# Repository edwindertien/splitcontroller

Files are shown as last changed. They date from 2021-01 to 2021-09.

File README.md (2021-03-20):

# splitcontroller
code and hardware files for a split level game controller

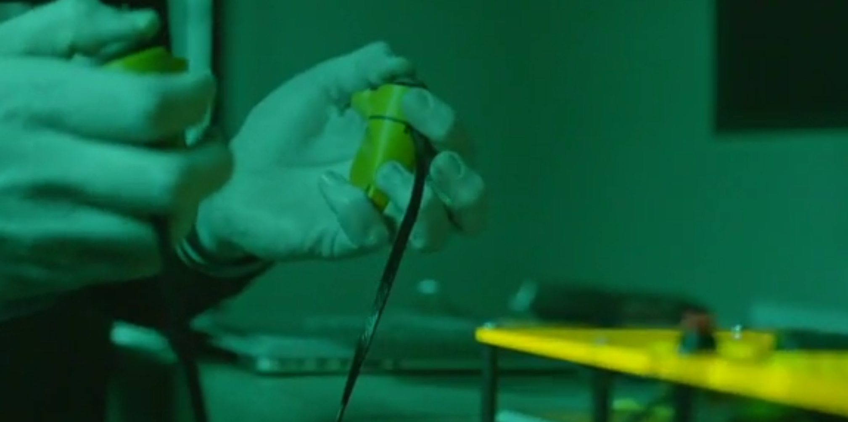
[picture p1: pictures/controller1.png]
dual hand-held controller with bridge box picture(c)IDTV(2021)
 

This project has been designed for a Duchenne patient who had progressive trouble operating his beloved regular PS4 controller. The original controller has been 'bridged' or patched by an Arduino Due (the PS4 controller works on 3.3V, so an Arduino with many inputs and outputs running at 3.3V is convenient). As new controller a split handheld system is used. This can be consisting of two Wii-nunchuck controllers or two custom 3D printed handheld controllers using (in this case) original PS4 joysticks. Currently this repository contains the following directories: 
  * bridge firmware: the firmware for the Arduino Due. Pinout is given in the header part of the code. The Wii-nunchuck functions are included in the code by Tod E. Kurt (2017) and modified for use on the DUE
  * remote arduino box: a simple laser cut 'sandwich' plate box containing a severely stripped-down ps4 controller, the arduino due and a 8000mAh powerbank. Included are some pictures and an svg file for cutting. Schematic drawing will follow. 
  * remote-modular ps4: an openSCAD script and printable STL files for a customisable hand-held design
  * remote-modular-switch: an openSCAD script and printable STL files for a customisable hand-held using the miniature nintendo-switch joystick

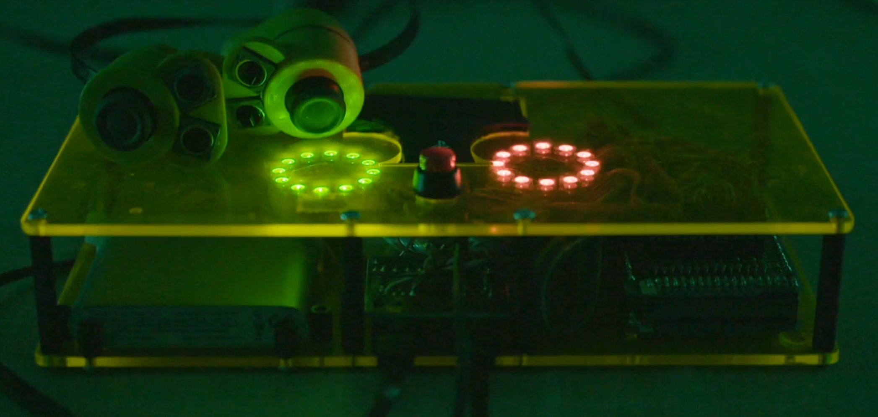
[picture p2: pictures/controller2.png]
bridge box, picture(c)IDTV(2021)
 

# bridge firmware
This code is meant for an Arduino Due which is used to take input signals from two handheld controllers, such as Wii-nunchucks or custom build controllers wired to A0--A7, and parse these signals to a modified PS4 controller. 

# remote arduino box
Simple laser cut 'sandwich' plate box containing a severely stripped-down ps4 controller, the arduino due and a 8000mAh powerbank. Further electonics consist of two 12-LED neopixel style ring-lights for feedback, a protoshield containing series resistors and RC filters for generating output signals to the PS4 controller. A small thin patching pcb for PS4 has been added to connect the Arduino due to the remnants of the PS4 controller. In order to connect two nunchucks to one I2C port, a PCA9540B I2C multiplexer has been added to the nice SMD proto-area of the used Adafruit Arduino MEGA protoshield. 

The parts used in the current version (as televised in 'We Gaan Het Maken')
  * Arduino Due
  * mega proto shield
  * 17 x resistor 1k (series resistor between outputs arduino to button inputs ps4)
  * 4 x resistor 100k (RC filter between analog outputs arduino to joystick inputs ps4)
  * 4 x capacitor 10uF (RC filter between analog outputs arduino to joystick inputs ps4)
  * PS4 remapper pcb (wired connection between arduino (shield) and ps4)
  * powerbank (8000mAh)
  * pushbutton (1 extra pushbutton to act as the PS4 button) on the box
  * 2 x RJ45 socket (to connect the custom handhelds) 

and for the handhelds:
  * 2 x flat UTP cable, 1 meter, black. 1 side has the plug, the other needs to be stripped into separate strands)
  * 3d printed parts: a handle, holder and top bit (and optional wedge)
  * a joystick. 1 option is a standard PS4 joystick (currently used) or a nintendo switch joystick (which needs a separate foil cable socket and adapter pcb to make connection) 
  * 2 x 12x14 mm pusbutton (large buttons have the easiest 'click')
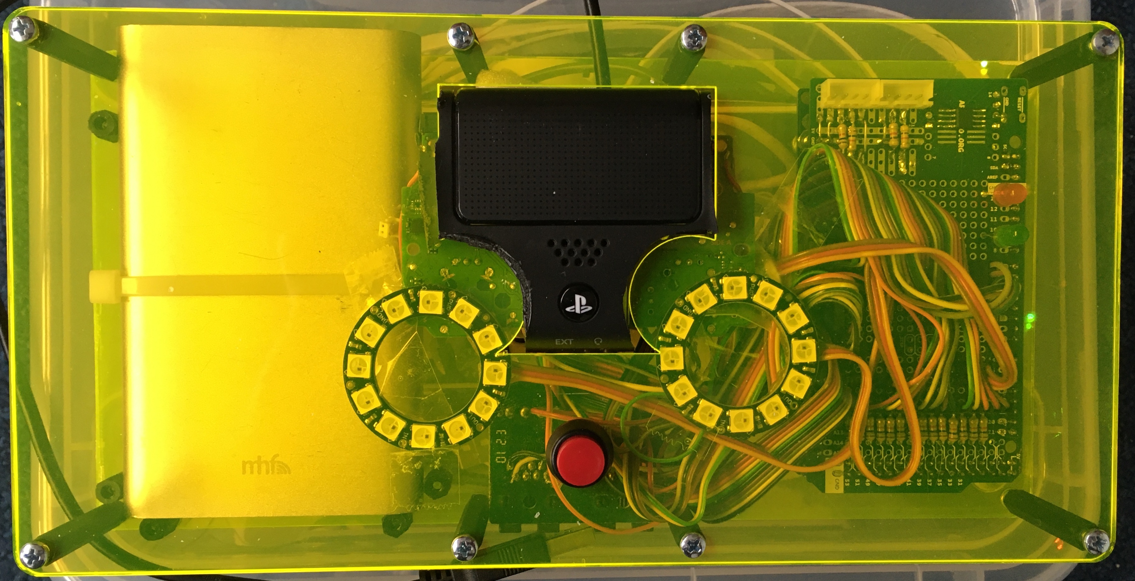
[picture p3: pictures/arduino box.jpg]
sandwich plate box with arduino, ps4 controller and powerbank
 

# remote-modular ps4
This directory contains an openSCAD script to generate a modular parametric hand-held controller using a standard PS4 joystick (replacement part) and two pushbuttons. For connectivity a flat (flexible) 6mm wide UTP cable has been used. Standard RJ45 plugs are used to connect these hand-helds to the arduino box. 

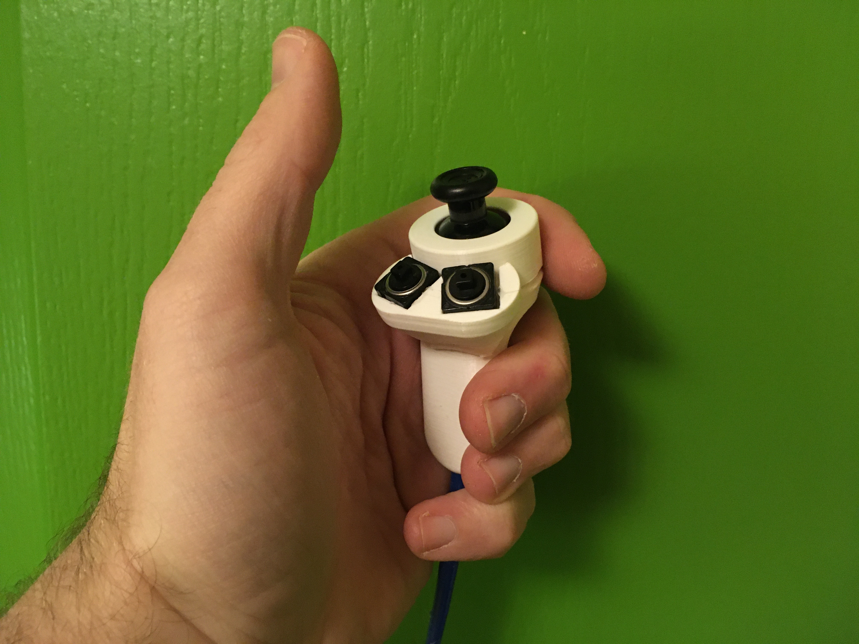
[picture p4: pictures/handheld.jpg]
3D printed handheld
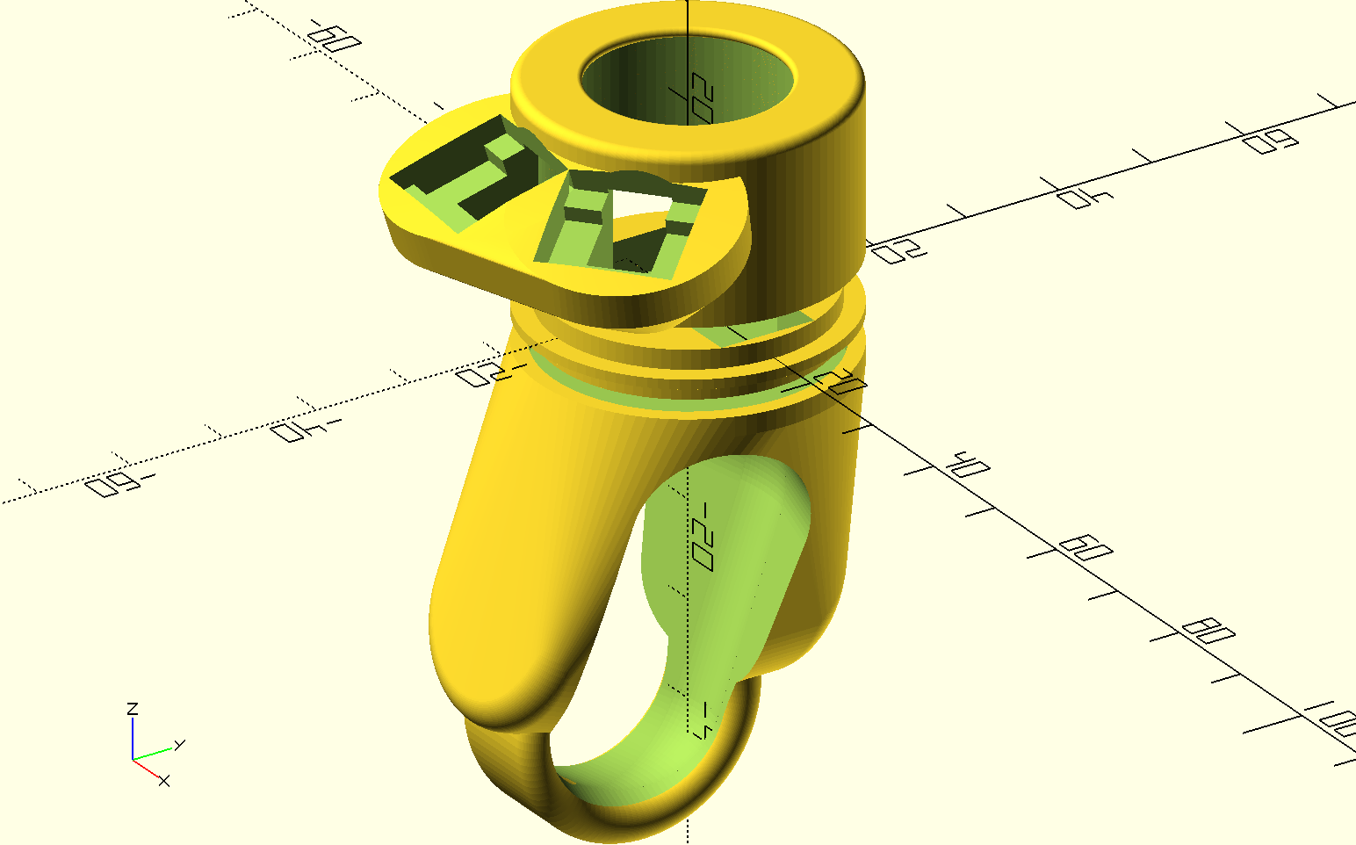
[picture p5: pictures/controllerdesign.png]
OpenSCAD design
 

# disclaimer
Hopefully stating the obvious: no guarantees can be given that these plans are correct or will work in your case or are safe. You will undoubtedly void the waranty on any PS4 controller you bought when you cut it down into functional bits and start adding wires and other functions. Re-selling any of this is probably actively prohibited by the Sony coorperation, so don't. Powering the device from a portable source such as a 5V power bank makes sense: Don't power wired handhelds with a supply directly connected to the mains. Maintain galvanic separation at all times (and if you don't know what that means, you should not be building this stuff).

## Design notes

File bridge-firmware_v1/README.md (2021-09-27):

The SD/LCD module code is used for an Arduino Due connected to a ReprapDiscount Smart Controller
This is a standard control panel for use on (for example) a Prusa MK3 printer
and contains a 4x20 character LCD display, rotary encoder, button, buzzer and SD card
slot.

The code assumes a pin-out as used on the RAMPS 1.4 arduino shield (normally for
Arduino MEGA). The only change is that on the DUE the SPI port is not mapped to pins
50, 51 and 52, but the ISP header at the center of the board has to be used

This code uses the standard built-in examples for Arduino, both for the LCD from
http://www.arduino.cc/en/Tutorial/LiquidCrystalHelloWorld
and the SD library 'file list' example.

Note that the DUE works on 3.3V but the display controller assumes 5V. It has a level
shifter (again) to operate the SD card on 3.3V. (I tried to make it work powered by 3.3V
although the display works, the SD card does not. The control board is hence powered by 5.0 V)

The following pin-out for the two 10-way EXP connectors on the display board are used:

```______________________________________
| EXP1 connector pin | Arduino DUE pin |
| 1 buzzer           | 37              |
| 2 ENCODER-button   | 35              |
| 3 LCD enable       | 17              |
| 4 LCD RS           | 16              |
| 5 LCD D4           | 23              |
| 6 LCD D5           | 25              |
| 7 LCD D6           | 27              |
| 8 LCD D7           | 29              |
| 9 GND              | GND             |
| 10 VCC             | +5V (not 3.3V!) |
|____________________|_________________|
______________________________________
| EXP2 connector pin | Arduino DUE pin |
| 1 MISO             | ISP pin 1 MISO  |
| 2 SCK              | ISP pin 3 SCK   |
| 3 ENCODER-1        | 31              |
| 4 ISP slave sel    | 53              |
| 5 ENCODER-2        | 33              |
| 6 MOSI             | ISP pin 4 MOSI  |
| 7 SD card detect   | 49              |
| 8 button           | 41              |
| 9 GND              | GND             |
| 10 NC              |                 |
|____________________|_________________|
```

(cc) e13, May 2021

************************************************************
SPLITCONTROLLER
************************************************************
Sketch for controlling a modified PS4 controller
using two nunchucks or analog nunchuck equivalent
(two hand-held controllers with two axis and two buttons)

2 nunChucks (multiplexed) using code from WiiChuckDemo by
2008 Tod E. Kurt, http://thingm.com/

Controller is Arduino Due, 1k series resistors are used
between PS4 buttons and Due outputs. All inputs are active-low
except R1, L1 and the Z-axes.

AnalogWrite is used to mimick joystick signals, RC low-pass
filters (10uF, 1k) have been used to make the analog signals

E13 - November 2020
--
```
Original nunchuck:  signal:    ext. cable    black nunchuck:
white -             ground     orange        white
red -               3.3+v      black         red
green -             data  A4   blue          blue
yellow -            clock A5   red           green

PCA 9540 pinout
      _____
SCL -|     |- SC1
SDA -|     |- SD1
VCC -|     |- GND
SD0 -|_____|- SC0
```

both the nunchucks and the PCA95040 can be powered from pins, 5V
For I2C using internal pull-up is sufficient

for the wired handheld controllers the following pinout
has been used: on RJ45 connectors:
```

1 analog_X
2 analog_Y
3 VCC
4 GND (switch)
5 GND (switch)
6 GND (potentiometer)
7 switch_1
8 switch_2
```

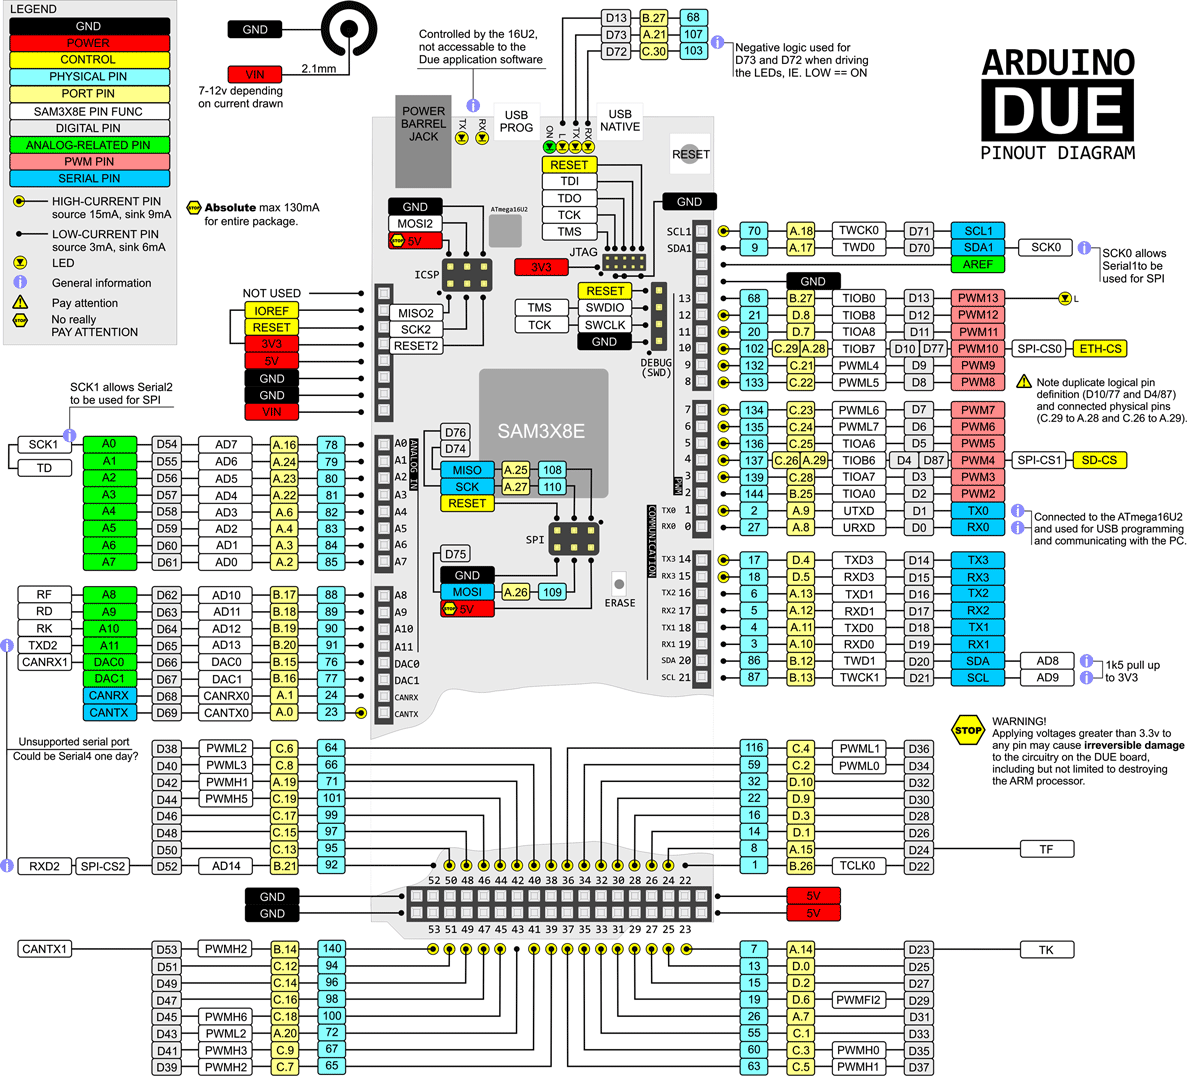
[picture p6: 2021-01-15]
remote-arduino box/documentation/Arduino-Due-Pinout.png

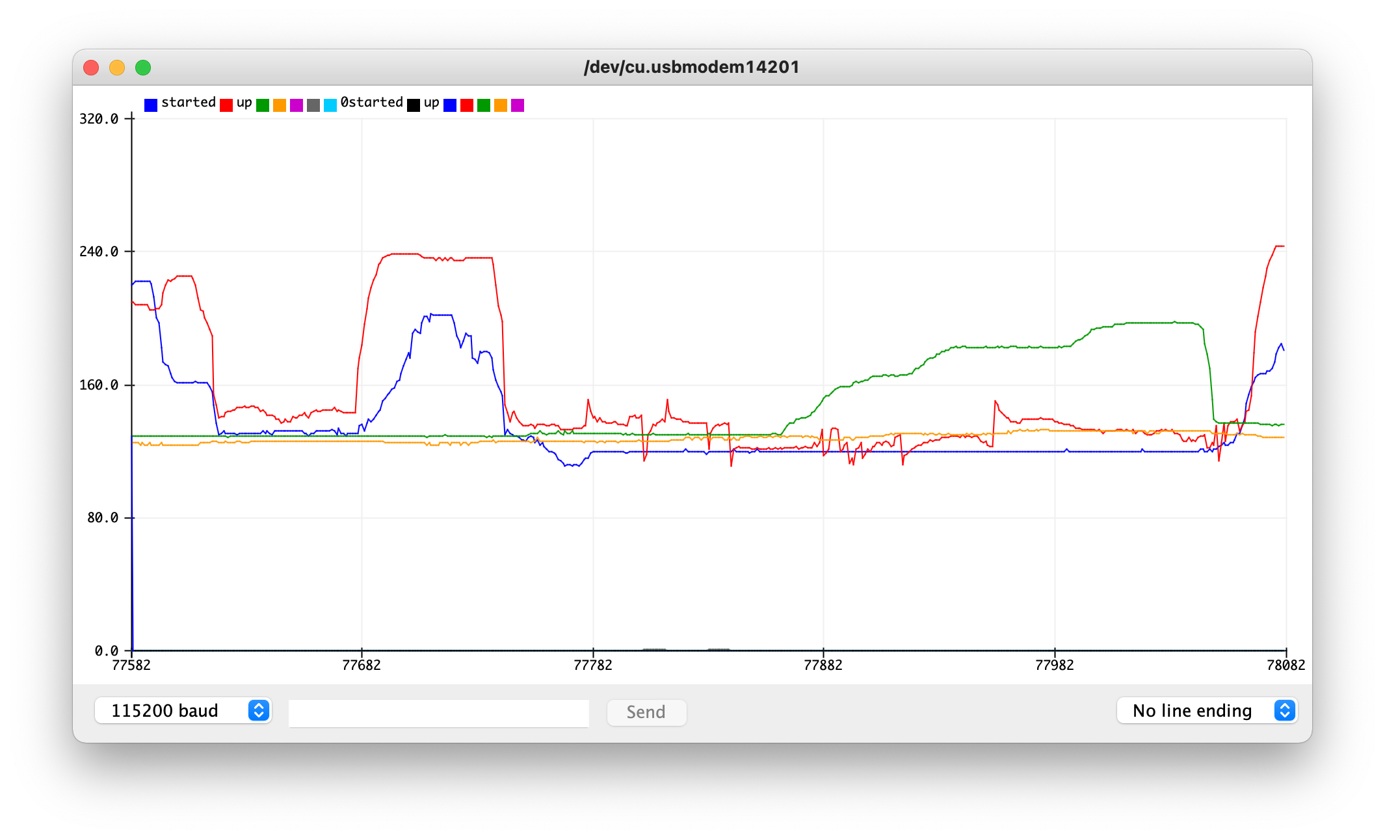
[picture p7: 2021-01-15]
pictures/analogjoystickdata.png

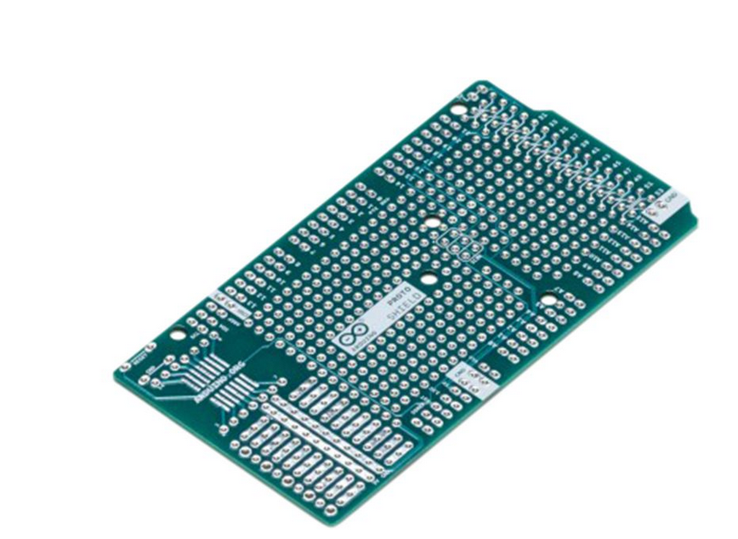
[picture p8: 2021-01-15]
pictures/protoshield.png

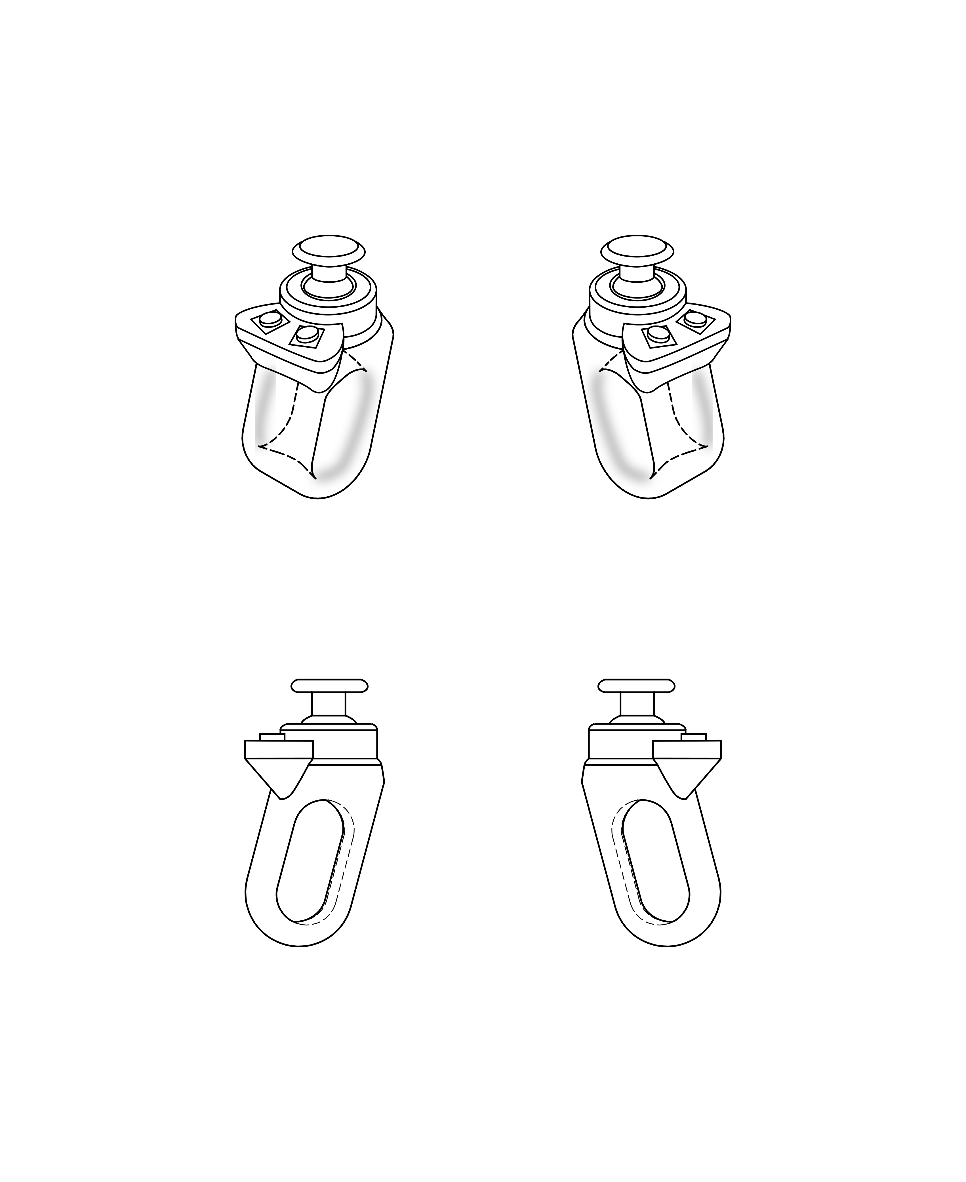
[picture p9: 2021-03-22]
pictures/new_controller_layout.png

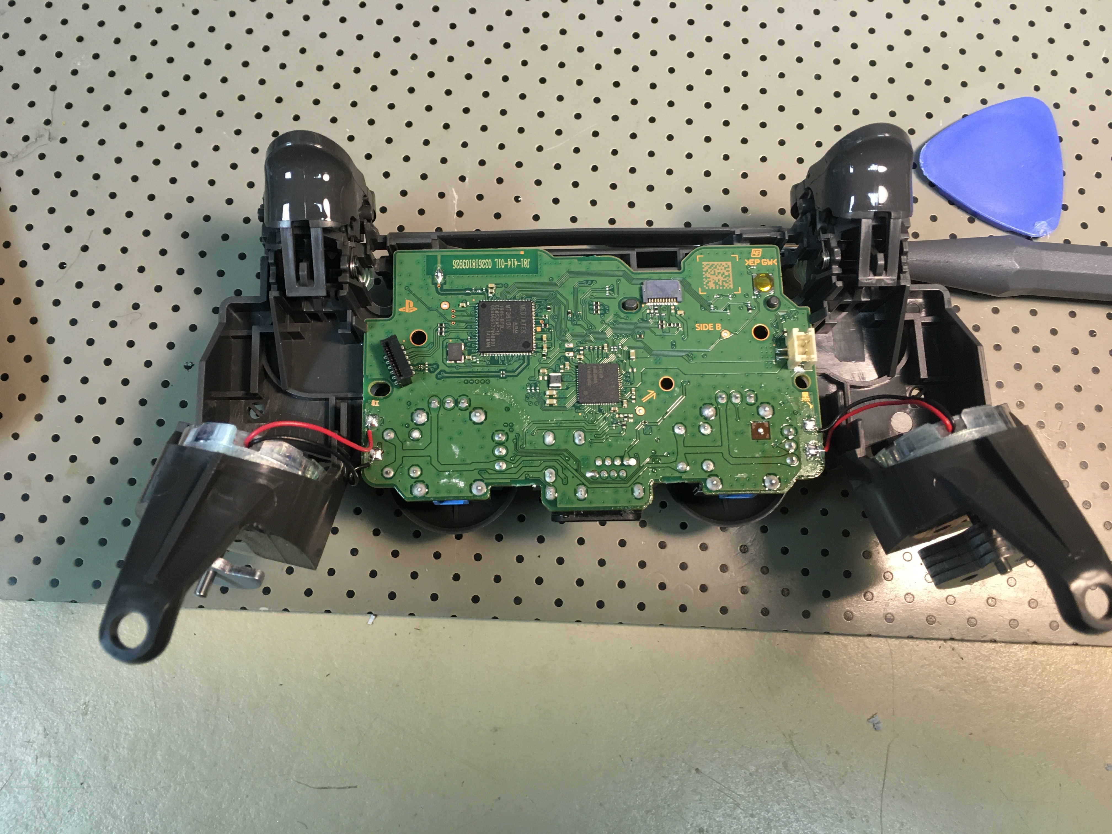
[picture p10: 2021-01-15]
pictures/strippedcontroller.jpg

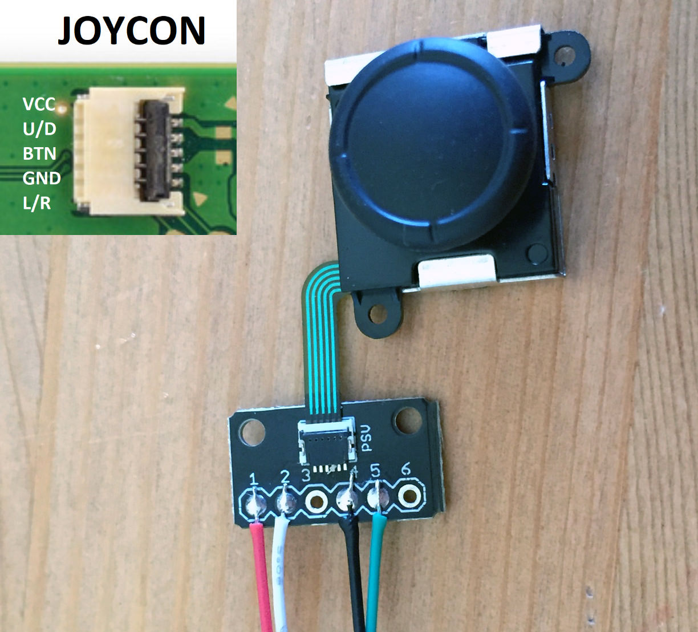
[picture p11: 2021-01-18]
remote-modular-switch/images/NAisoG4.jpg

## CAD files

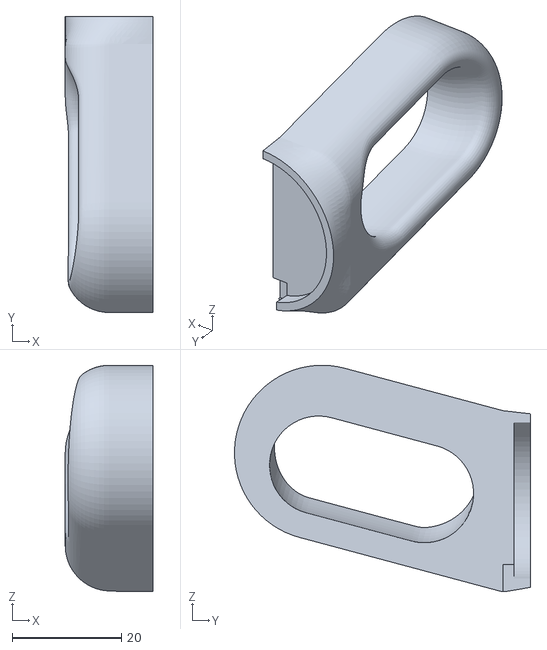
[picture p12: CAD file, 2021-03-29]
remote-modular-ps4/export/rounded_version_half_mesh1.stl
16.0 x 54.1 x 41.4

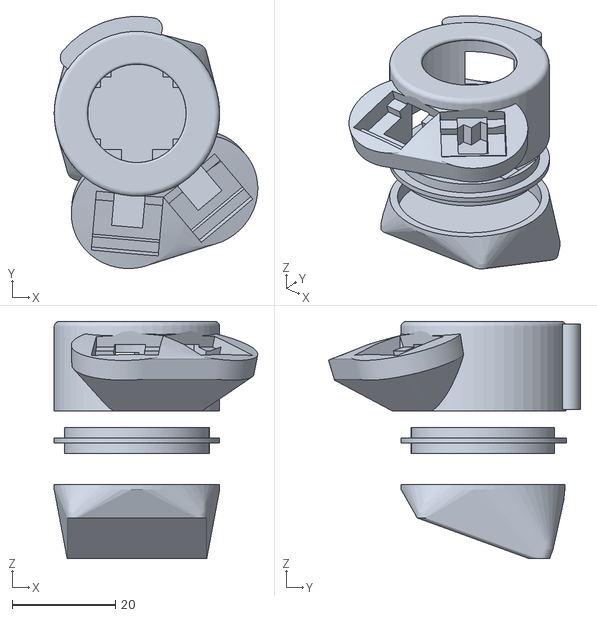
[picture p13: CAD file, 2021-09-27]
remote-modular-ps4/modularremote_adjusted_piece.stl
39.4 x 48.7 x 45.9

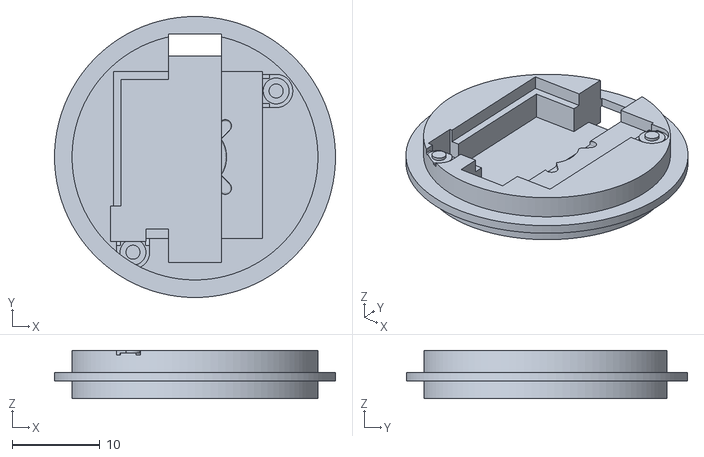
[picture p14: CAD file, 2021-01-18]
remote-modular-switch/export/switch-holder.stl
32.0 x 32.0 x 5.50

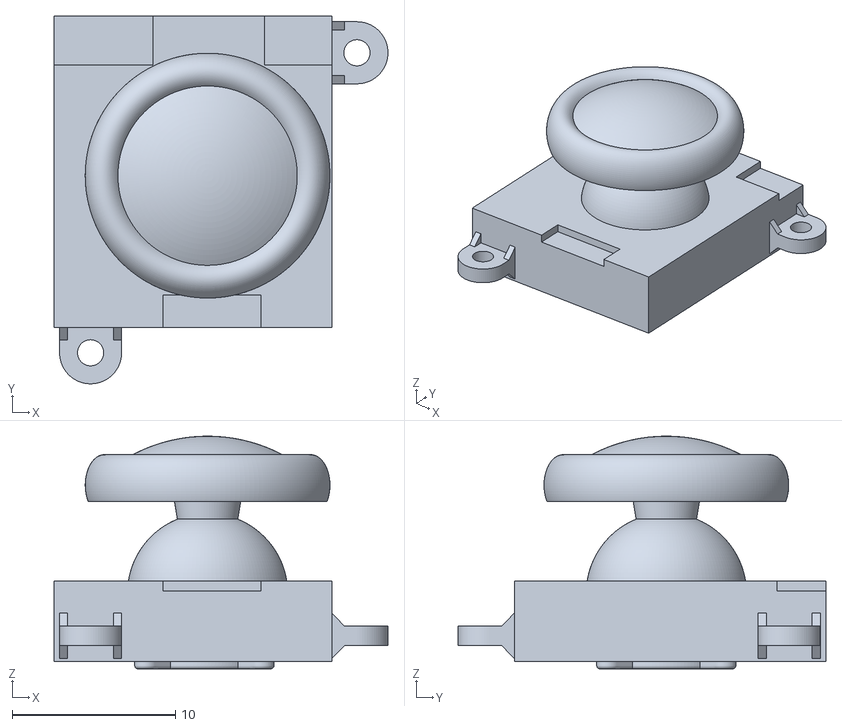
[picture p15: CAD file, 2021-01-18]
remote-modular-switch/export/joycon.stl
20.4 x 22.5 x 14.2

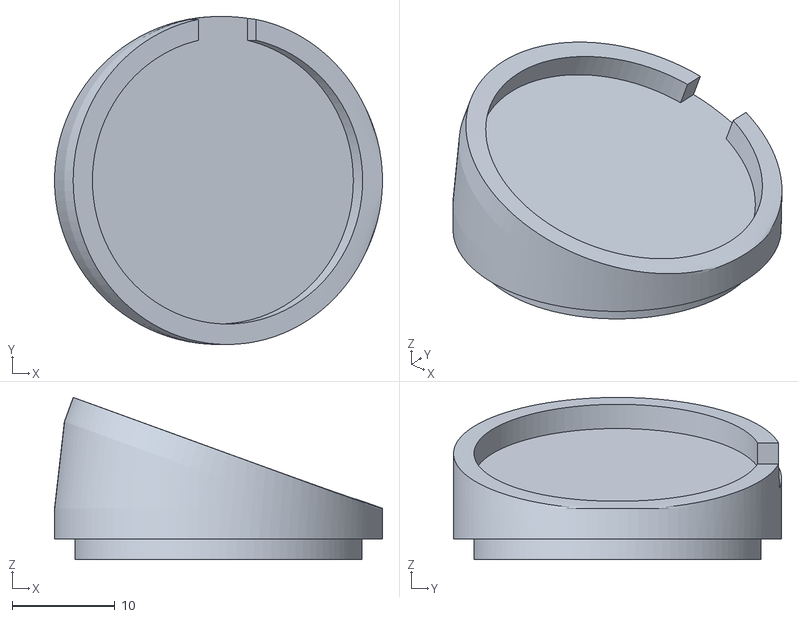
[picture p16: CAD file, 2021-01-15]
remote-modular-ps4/export/wedge20.stl
32.0 x 32.0 x 15.8

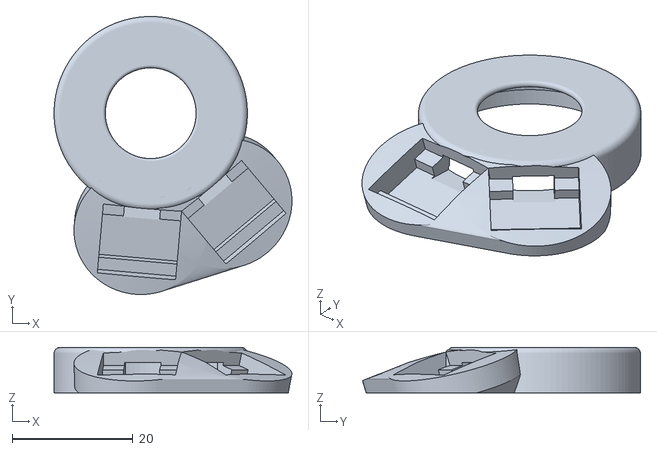
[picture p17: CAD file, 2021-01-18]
remote-modular-switch/export/switch-top.stl
39.4 x 46.0 x 7.53

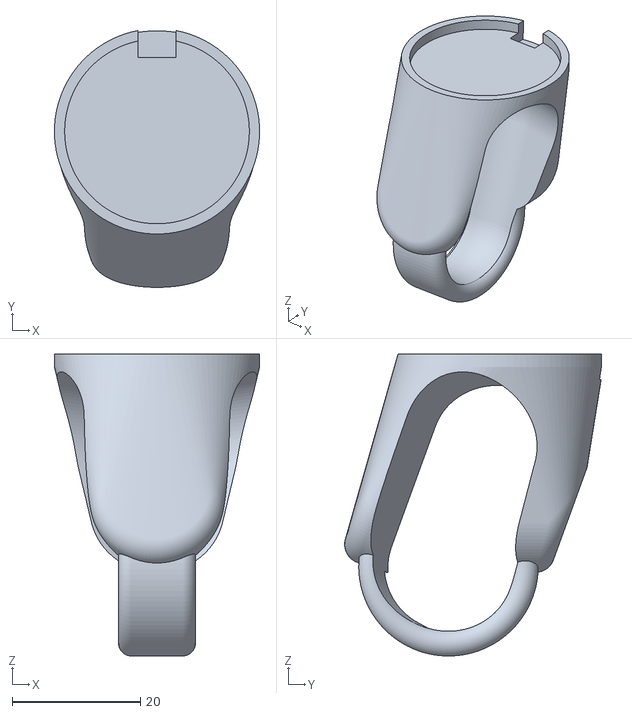
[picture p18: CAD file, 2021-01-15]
remote-modular-ps4/export/modularremote-beugelring.stl
32.0 x 40.0 x 47.1

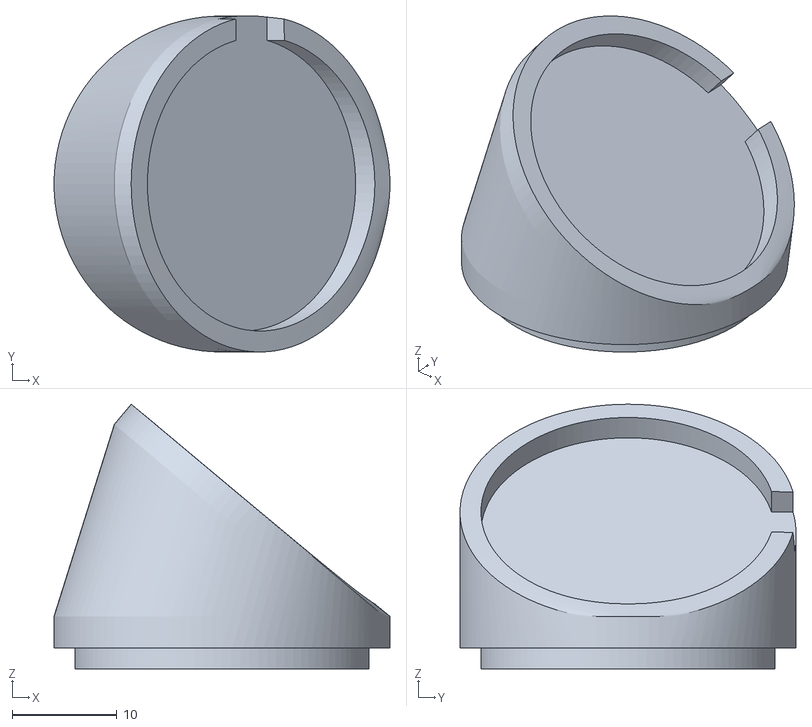
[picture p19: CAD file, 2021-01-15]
remote-modular-ps4/export/wedge40.stl
32.0 x 32.0 x 25.2

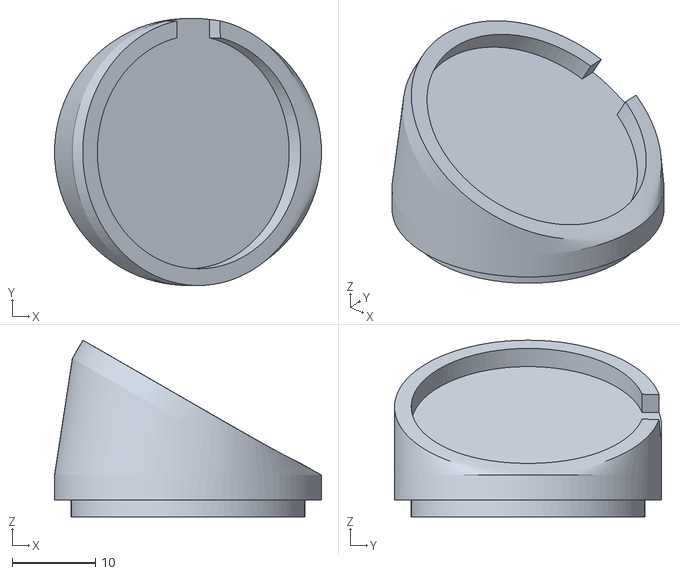
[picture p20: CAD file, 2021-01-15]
remote-modular-ps4/export/wedge30.stl
32.0 x 32.0 x 21.2

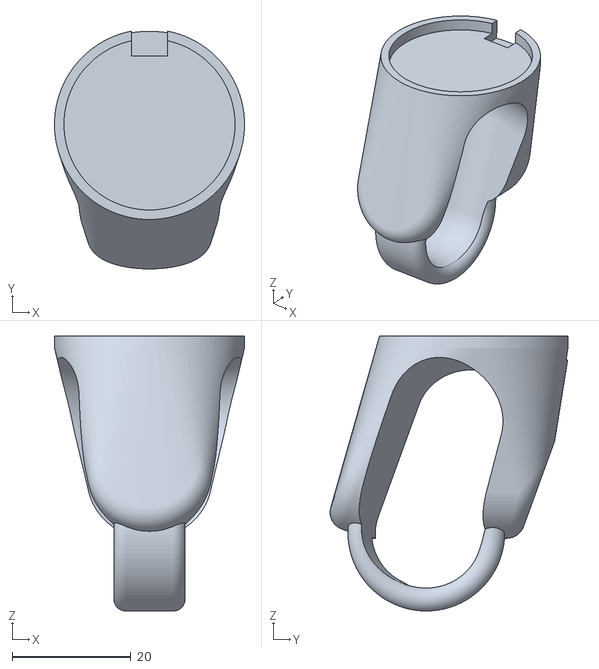
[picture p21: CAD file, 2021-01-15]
remote-modular-ps4/export/modularremote-beugelring-18.4.stl
32.0 x 40.0 x 46.3

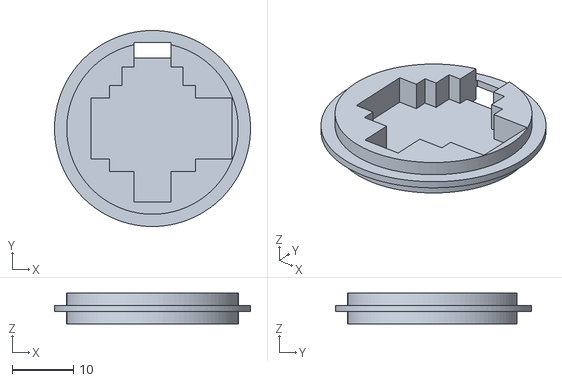
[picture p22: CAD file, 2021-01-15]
remote-modular-ps4/export/modularremote-holder.stl
32.0 x 32.0 x 5.00

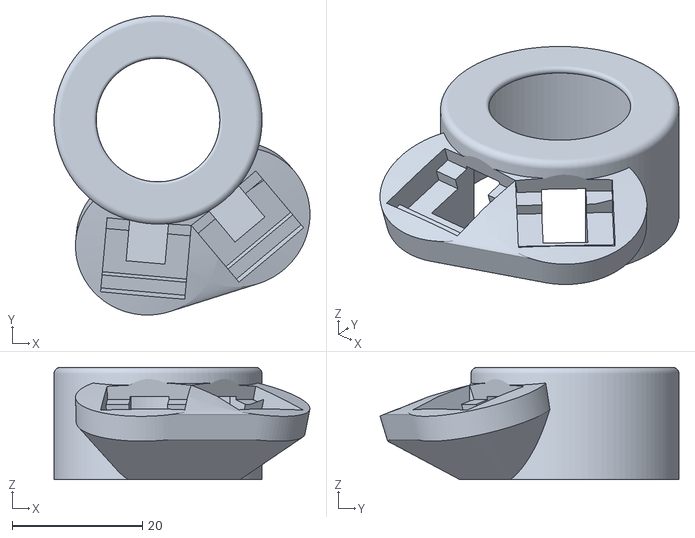
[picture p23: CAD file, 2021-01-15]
remote-modular-ps4/export/modularremote-top.stl
39.4 x 46.0 x 17.3

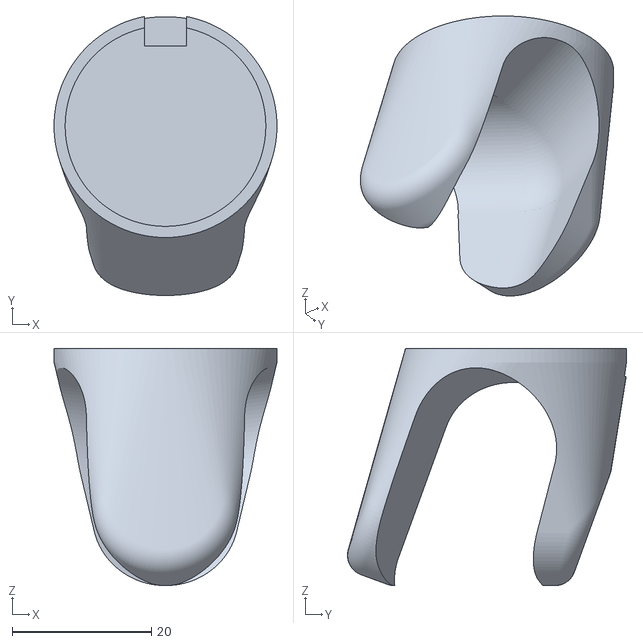
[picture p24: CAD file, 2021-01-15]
remote-modular-ps4/export/handle.stl
32.0 x 40.0 x 34.0

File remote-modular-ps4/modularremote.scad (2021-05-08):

// change to 100 for better rendering
$fn = 20;



diameter = 18;
translate([0,0,4])top();
translate([0,0,2])holder();
translate([0,0,-6])beugel(20);
//wedge(60);  // between 10 and 60

//cup(0,0);
module ring(){
  difference() {
        union(){
            translate([0,0,2])cylinder(d = 32, h = 2);
            cheese(15,1,2);
        }
         translate([0, 0, 2])cylinder(d = 28.8, h = 10);
            translate([-3, 11.5, -2])cube([6, 5, 10]);
        
        }
         

         translate([-3,0,-11])rotate([90,0,90])doughnut(11,1.5,6);
    }      

module top() {
    difference(){
        union(){
            color( "Lime", 1.0 )
            rotate_extrude() {
                hull() {
                    translate([15, 17.5, 0]) circle(r = 1);
                    translate([10, 18, 0]) circle(r = 0.5);
                }
                hull() {
                    translate([15, 17.5, 0]) circle(r = 1);
                    translate([15, 0, 0]) circle(r = 1);
                }     
            } 
               translate([0,0,8])  
            color( "Red", 1.0 )hull(){
rotate([0,0,-5])translate([0,-14,-2])sphere(d=12);
rotate([0,0,40])translate([0,-14,-2])sphere(d=12);
      
rotate([0,0,-5])translate([0,-14,-12])rotate([17,0,0])translate([0,0,15])cylinder(d1=22,d2=22,h=4);
rotate([0,0,40])translate([0,-14,-12])rotate([17,0,0])translate([0,0,15])cylinder(d1=22,d2=22,h=4);      
      }
      // here goes thing for third button
      color( "PaleVioletRed", 1.0 )rotate([0,0,80])translate([0,0,-10])minkowski()
{
  rotate_extrude(angle = 60, convexity = 2)translate([16,20,0])square([1,10],center=true);
  cylinder(r=2,h=1);
}


        }
        translate([-20,-20,-5])cube([40,40,5]);
        cylinder(d=28,h=17.5);
        
        translate([0,0,8]){
              rotate([0,0,-5])translate([-6.5,-26.5,2])rotate([17,0,0])cube([13,12,5]);
  rotate([0,0,40])translate([-6.5,-26.5,2])rotate([17,0,0])cube([13,12,5]);
         
                       rotate([0,0,-5])translate([-6.5,-24,1])rotate([17,0,0])cube([13,7.5,5]);
            
  rotate([0,0,40])translate([-6.5,-24,1])rotate([17,0,0])cube([13,7.5,5]);   
            
            
  rotate([0,0,-5])translate([-3,-22,-4])cube([6,22,10]);
  rotate([0,0,40])translate([-3,-22,-4])cube([6,22,10]);
        }
      cylinder(d=28.4,h=4.5);//better fit  
      translate([-20,-20,0])cube([40,40,1.2]);  
    }

}
module wedge(angle){
difference(){
union(){
cylinder(d=28,h=3);
hull(){
translate([0,0,2])cylinder(d=32,h=3);
translate([angle/20,0,8+(angle-20)/3])rotate([0,angle,0])cylinder(d=32,h=2.5);
}
}
translate([angle/20,0,8+(angle-20)/3])rotate([0,angle,0])cylinder(d=28,h=3.1);
translate([angle/20,0,8+(angle-20)/3])rotate([0,angle,0])translate([-3,10,0])cube([6,30,5]);
}
}



module holder(){
difference() {
    union(){
    translate([0,0,-3])cylinder(d = 32, h = 1);
    translate([0,0,-5])cylinder(d=28,h=5);  
  }
  translate([-20, 0, -15])rotate([-10, 0, 0])
  union() {
    rotate([0, 90, 0])cylinder(d = 20, h = 40);
    translate([0, -10, -60])cube([40, 20, 60]);
  }
  translate([-7,-7,-4])potmeters();
  translate([0,0,1])cylinder(d=26,h=2);
//   rotate([0,0,-5])translate([-3,-22,-3])cube([6,22,10]);
//  rotate([0,0,40])translate([-3,-22,-3])cube([6,22,10]);
  //translate([0,-20,-50])rotate([-10,0,0])cylinder(d=5,h=70);
  translate([-3,11.5,-5])cube([6,2.5,10]); 
 translate([-3,-12,-4])cube([6,24,10]); 
}
}
//beugel(20);
module beugel(angle) {
    
  difference() {
    union() {

      hull() {
        cylinder(d = 32, h = 2);
        translate([0, -15, -22])rotate([90-angle, 0, 0])cheese(r1 = 10 - 2.5, r2 = 3, h = 4);
                  translate([0, 8, -22])rotate([90-angle, 0, 0])cheese(r1 = 10 - 2.5, r2 = 3, h = 4);
      }
     rotate([-angle, 0, 0])translate([-4,3,-32])rotate([0,90,0])doughnut(diameter/2+2,2,8);
    }

    
    translate([0, 0, -13])rotate([-angle, 0, 0])
    fingercutout(45,20);
    
    translate([0, 0, -0.3])cylinder(d = 28.8, h = 10);
    translate([-3, 11.5, -2])cube([6, 5, 10]);
  }
}


module handle(angle) {
    
  difference() {
    union() {

      hull() {
        cylinder(d = 32, h = 2);
        translate([0, -15, -22])rotate([90-angle, 0, 0])cheese(r1 = 10 - 2.5, r2 = 3, h = 4);
                  translate([0, 8, -22])rotate([90-angle, 0, 0])cheese(r1 = 10 - 2.5, r2 = 3, h = 4);
      }

    }

    
    translate([0, 0, -13])rotate([-angle, 0, 0])
    fingercutout(45,20);
    
    translate([0, 0, 0])cylinder(d = 28.8, h = 10);
    translate([-3, 11.5, -2])cube([6, 2.5, 10]);
    translate([-3, 11.5, -2])cube([6, 5, 10]);
  }
}



module fingercutout(angle,height){
    
    translate([0,0,-height])cylinder(d=diameter,h=height);
    translate([0,0,0])sphere(d=diameter);
    translate([0,0,-height])sphere(d=diameter);
    rotate([0,0,angle/2])translate([-40,0,0])
    union() {
      rotate([0, 90, 0])cylinder(d = diameter, h = 40);
       translate([0,0,-height])rotate([0, 90, 0])cylinder(d = diameter, h = 40);
       translate([0,-diameter/2,-height])cube([40,diameter,height]); 
    }

    rotate([0,0,-angle/2])translate([0,0,0])
        union() {
      rotate([0, 90, 0])cylinder(d = diameter, h = 40);
      translate([0,0,-height])rotate([0, 90, 0])cylinder(d = diameter, h = 40);
                  translate([0,-diameter/2,-height])cube([40,diameter,height]);
    }
}    

module originalhandle() {
  difference() {
    union() {

      hull() {
        cylinder(d = 32, h = 2);
        translate([0, -15, -35])rotate([80, 0, 0])cheese(r1 = 10 - 2.5, r2 = 3, h = 4);
      }

    }
    translate([0, 0, 0])cylinder(d = 28.8, h = 10);
    translate([-20, 0, -11])rotate([-10, 0, 0])

    union() {
      rotate([0, 90, 0])cylinder(d = 20, h = 40);
      translate([0, -10, -60])cube([40, 20, 60]);
    }
    translate([-3, 11.5, -5])cube([6, 2.5, 10]);
  }
}

//translate([-40,0,0])cylinder(d=24,h=8);
module cup(x,y){translate([0, 0, 5])rotate([x,y, 0]) {
  translate([0, 0, 5]) {
    translate([0, 0, 14]) {
      difference() {
        cheese(6.5, 2.5, 0);
        translate([0, 0, 26])sphere(d = 50);
      }
    }
    translate([0, 0, 5])cylinder(d = 9, h = 8);
    translate([0, 0, -7])difference() {
      sphere(d = 28);
      translate([-15, -15, -15])cube([30, 30, 22]);
    }
  }
}
}



module potmeters(){
translate([-3,2,0])cube([23,10,14]);

translate([2,1,0])cube([10,16,14]);

cube([14,14,14]);

}




module doughnut(r1, r2, h) {
  rotate_extrude() {
    hull() {
      translate([r1, h, 0])circle(r = r2);
      translate([r1, 0, 0])circle(r = r2);
    }
  }
}

module cheese(r1, r2, h) {
  hull() {
    rotate_extrude() {
      translate([r1, h, 0])circle(r = r2);
      translate([r1, 0, 0])circle(r = r2);
    }
  }
}

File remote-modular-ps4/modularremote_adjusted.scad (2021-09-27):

/* change $fn to 100 for better quality rendering
ONLY do this for final version, because minkowski gives your computer
a hard time, and a long wait for you.
*/
$fn = 50;
fragsstd = 100;
fragsminkw = 50;

fingercutoutdeg = 45;
fingercutouthght = 20;

diameter = 18;
translate([0,0,4])top();
translate([0,0,2])holder();
translate([0,0,-12])beugel(20);
//wedge(60);  // between 10 and 60
   


module top() {
       //thirdbuttoncontainer();
    difference(){
        union($fn=fragsstd){
            color( "Lime", 1.0 )
            rotate_extrude( $fn=50) {
                hull() {
                    translate([15, 17.5, 0]) circle(r = 1, $fn=fragsstd );
                    translate([10, 18, 0]) circle(r = 0.5, $fn=fragsstd );
                }
                hull() {
                    translate([15, 17.5, 0]) circle(r = 1, $fn=fragsstd );
                    translate([15, 0, 0]) circle(r = 1, $fn=fragsstd );
                }     
            } 
               translate([0,0,8])  
            color( "Red", 1.0 )hull($fn=fragsstd ){
rotate([0,0,-5])translate([0,-14,-2])sphere(d=12);
rotate([0,0,40])translate([0,-14,-2])sphere(d=12);
      
rotate([0,0,-5])translate([0,-14,-12])rotate([17,0,0])translate([0,0,15])cylinder(d1=22,d2=22,h=4, $fn=fragsstd );
rotate([0,0,40])translate([0,-14,-12])rotate([17,0,0])translate([0,0,15])cylinder(d1=22,d2=22,h=4, $fn=fragsstd );      
      }
      thirdbuttonelement(); 



        }
        translate([-20,-20,-5])cube([40,40,5]);
        // upper inner cylinder
         color( "RosyBrown", 1.0 ) cylinder(d=28,h=17.5);
        
        // third button container
        
        thirdbuttoncontainer();
        
        // button containers
           translate([0,0,8]){
             color( "RosyBrown", 1.0 ) rotate([0,0,-5])translate([-6.5,-26.5,2])rotate([17,0,0])cube([13,12,5]);
  color( "RosyBrown", 1.0 )rotate([0,0,40])translate([-6.5,-26.5,2])rotate([17,0,0])cube([13,12,5]);
         
                       rotate([0,0,-5])translate([-6.5,-24,1])rotate([17,0,0])cube([13,7.5,5]);
            
  rotate([0,0,40])translate([-6.5,-24,1])rotate([17,0,0])cube([13,7.5,5]);   
            
            
  color( "Tan", 1.0 )rotate([0,0,-5])translate([-3,-22,-4])cube([6,22,10]);
 color( "Tan", 1.0 ) rotate([0,0,40])translate([-3,-22,-4])cube([6,22,10]);
        }
        // bottom inner cylinder
       color( "Teal", 1.0 ) cylinder(d=28.4,h=4.5);//better fit  
        // flattened bottom
       color( "Tan", 1.0 ) translate([-20,-20,0])cube([40,40,1.2]);  
    }
    
    module thirdbuttoncontainer() {
          color( "OliveDrab", 0.5 )rotate([90,0,20])translate([-7,3,-22])
        union() {
        cube([13,12,7]);
           color( "DarkOrange", 1.0 )translate([0,2,-1]) cube([13,7.5,10]);
        }
    }
    
    module thirdbuttonelement() {
              color( "PaleVioletRed", 1.0 )rotate([0,0,80])translate([0,0,-11])
        minkowski($fn = fragsminkw)
        {
          rotate_extrude(angle = 60, convexity = 2)translate([16,20,-15])square([1.5,15],center=true);
          cylinder(r=2,h=1.5);
        }
        
    }

}
module wedge(angle){
difference(){
union(){
cylinder(d=28,h=3);
hull(){
translate([0,0,2])cylinder(d=32,h=3);
translate([angle/20,0,8+(angle-20)/3])rotate([0,angle,0])cylinder(d=32,h=2.5);
}
}
translate([angle/20,0,8+(angle-20)/3])rotate([0,angle,0])cylinder(d=28,h=3.1);
translate([angle/20,0,8+(angle-20)/3])rotate([0,angle,0])translate([-3,10,0])cube([6,30,5]);
}
}



module holder(){
difference() {
    union(){
    translate([0,0,-3])cylinder(d = 32, h = 1, $fn=fragsstd );
    translate([0,0,-5])cylinder(d=28,h=5, $fn=fragsstd );  
  }
  translate([-20, 0, -15])rotate([-10, 0, 0])
  union() {
    rotate([0, 90, 0])cylinder(d = 20, h = 40,  $fn=fragsstd );
    translate([0, -10, -60])cube([40, 20, 60]);
  }
  translate([-7,-7,-4])potmeters();
  translate([0,0,1])cylinder(d=26,h=2);
  translate([-3,11.5,-5])cube([6,2.5,10]); 
 translate([-3,-12,-4])cube([6,24,10]); 
}
}

module beugel(angle) {
    szbeugel = diameter + 5;
    szbeugelhght = fingercutouthght*2-5 ;
    hght =  szbeugelhght ;
color( "Coral", 1.0 )toppiece();
        
    translate([0,0,-7])
        minkowski()
        {

            
            difference() {
                rotate([-angle,0,0])
                union() {
                    
                    translate([0,0,-szbeugelhght/2])cube(size = [szbeugel,szbeugel,szbeugelhght], center = true);
                    translate([-szbeugel/2,0,-hght])rotate([0,90,0])cylinder(d = szbeugel, h = szbeugel);
                }
                translate([0, 0, -13])rotate([-angle, 0, 0])
                fingercutout(45,fingercutouthght);
            }
          cylinder(r=2,h=1);
        }
    
        
        module toppiece() {
            difference() {
            hull() {
                translate([0,0,2])cylinder(d = 32, h = 1);
                minkowski($fn = fragsminkw) {
                    rotate([-angle,0,0])translate([0,2.5,-6])cube(size = [szbeugel,szbeugel,2], center = true);
                    cylinder(r=2,h=1, $fn = fragsstd);
                }
            }
            // cuts
                translate([0, 0, -0.3])color( "PaleVioletRed", 1.0 )cylinder(d = 28.8, h = 10, $fn = fragsstd);
        translate([-3, 11.5, -2])color( "PaleVioletRed", 1.0 )cube([6, 5, 10]);
            
        }
        }
    
}

module handle(angle) {
    
  difference() {
    union() {

      hull() {
        cylinder(d = 32, h = 2);
        translate([0, -15, -22])rotate([90-angle, 0, 0])cheese(r1 = 10 - 2.5, r2 = 3, h = 4);
                  translate([0, 8, -22])rotate([90-angle, 0, 0])cheese(r1 = 10 - 2.5, r2 = 3, h = 4);
      }

    }

    
    translate([0, 0, -13])rotate([-angle, 0, 0])
    fingercutout(45,20);
    
    translate([0, 0, 0])cylinder(d = 28.8, h = 10);
    translate([-3, 11.5, -2])cube([6, 2.5, 10]);
    translate([-3, 11.5, -2])cube([6, 5, 10]);
  }
}


module fingercutout(angl,height){
    radius = diameter /2;
    translate([0,-22,-height])
    rotate([0,0,67])element();
    module element() {
    translate([20,0,0])rotate([90,0,0])linear_extrude(height = 40)section();
    rotate_extrude(angle = 45,convexity = 10)translate([20,0,0])section();
    rotate([90,0,45])translate([20,0,-40])linear_extrude(height = 40)section();
       module section() {
         hull() {
          translate([0, height, 0])circle(r = radius);
          translate([0, 0, 0])circle(r = radius);
            }
        }

    }
}    

   



module potmeters(){
translate([-3,2,0])cube([23,10,14]);

translate([2,1,0])cube([10,16,14]);

cube([14,14,14]);

}




module doughnut(r1, r2, h) {
  rotate_extrude() {
    hull() {
      translate([r1, h, 0])circle(r = r2);
      translate([r1, 0, 0])circle(r = r2);
    }
  }
}

module cheese(r1, r2, h) {
  hull() {
    rotate_extrude() {
      translate([r1, h, 0])circle(r = r2);
      translate([r1, 0, 0])circle(r = r2);
    }
  }
}

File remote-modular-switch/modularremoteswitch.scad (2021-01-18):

$fn = 100;
translate([0,0,5])top();
//translate([0,0,2])holder();
 
 //translate([-9.3,-9.3,0])import("joycon.stl");
//translate([0,0,-10])handle(20);
//cup(0,0);
module ring(){
  difference() {
        union(){
            translate([0,0,2])cylinder(d = 32, h = 2);
            cheese(15,1,2);
        }
         translate([0, 0, 2])cylinder(d = 28.8, h = 10);
            translate([-3, 11.5, -2])cube([6, 5, 10]);
        
        }
         

         translate([-3,0,-11])rotate([90,0,90])doughnut(11,1.5,6);
    }        

module top() {
    difference(){
        union(){
            rotate_extrude() {
                hull() {
                    translate([15, 8.5, 0]) circle(r = 1);
                    translate([8, 9, 0]) circle(r = 0.5);
                }
                hull() {
                    translate([15, 8.5, 0]) circle(r = 1);
                    translate([15, 0, 0]) circle(r = 1);
                }     
            } 
            
            // and now for the buttons
               translate([0,0,1])  
            difference(){
            hull(){
rotate([0,0,-5])translate([0,-14,-2])sphere(d=12);
rotate([0,0,40])translate([0,-14,-2])sphere(d=12);
      
rotate([0,0,-5])translate([0,-14,-12])rotate([17,0,0])translate([0,0,15])cylinder(d1=22,d2=22,h=4);
rotate([0,0,40])translate([0,-14,-12])rotate([17,0,0])translate([0,0,15])cylinder(d1=22,d2=22,h=4);      
      }
      cylinder(d=28,h=20);
  }
        }
        
        translate([-20,-40,-10])cube([50,60,12]);
        
        
        translate([0,0,1]){
              rotate([0,0,-5])translate([-6.5,-26.5,2])rotate([17,0,0])cube([13,12,5]);
  rotate([0,0,40])translate([-6.5,-26.5,2])rotate([17,0,0])cube([13,12,5]);
         
                       rotate([0,0,-5])translate([-6.5,-24,1])rotate([17,0,0])cube([13,7.5,5]);
            
  rotate([0,0,40])translate([-6.5,-24,1])rotate([17,0,0])cube([13,7.5,5]);   
            
            
  rotate([0,0,-5])translate([-3,-22,3])cube([6,22,3]);
  rotate([0,0,40])translate([-3,-22,3])cube([6,22,3]);
        } 
        
        // and the lower edges
      cylinder(d=28.4,h=4.5);//better fit  
      translate([-20,-20,0])cube([40,40,1.8]);  
    }

}

module holder(){
difference() {
    union(){
    translate([0,0,-3])cylinder(d = 32, h = 1);
    translate([0,0,-5])cylinder(d=28,h=5.5);  
  }
  translate([-20, 0, -15])rotate([-10, 0, 0])
  union() {
    rotate([0, 90, 0])cylinder(d = 20, h = 40);
    translate([0, -10, -60])cube([40, 20, 60]);
  }
  //translate([-7,-7,-4])potmeters();
  translate([0,0,1])cylinder(d=26,h=2);
  translate([-9.3,-9.3,-1])import("joycon.stl");
//  translate([-9,-9,-1])import("joycon.stl");
//  translate([-9,-9,-2])import("joycon.stl");
  //translate([-6.8,-10.8,-2])cylinder(d=3.5,h=5);
  
  translate([-3,11.5,-5])cube([6,2.5,10]); 
 translate([-3,-12,-4])cube([6,24,10]); 
  
  translate([-8.4,-8.2,-4])cube([10.5,17,4]);
  translate([-9.6,-9.6,-4])cube([4,4,10]);
}
}
//beugel(20);
module beugel(angle) {
    
  difference() {
    union() {

      hull() {
        cylinder(d = 32, h = 2);
        translate([0, -15, -22])rotate([90-angle, 0, 0])cheese(r1 = 10 - 2.5, r2 = 3, h = 4);
                  translate([0, 8, -22])rotate([90-angle, 0, 0])cheese(r1 = 10 - 2.5, r2 = 3, h = 4);
      }
     rotate([-angle, 0, 0])translate([-4,3,-32])rotate([0,90,0])doughnut(12,2,8);
    }

    
    translate([0, 0, -13])rotate([-angle, 0, 0])
    fingercutout(45,20);
    
    translate([0, 0, 0])cylinder(d = 28.8, h = 10);
    translate([-3, 11.5, -2])cube([6, 5, 10]);
  }
}


module handle(angle) {
    
  difference() {
    union() {

      hull() {
        cylinder(d = 32, h = 2);
        translate([0, -15, -22])rotate([90-angle, 0, 0])cheese(r1 = 10 - 2.5, r2 = 3, h = 4);
                  translate([0, 8, -22])rotate([90-angle, 0, 0])cheese(r1 = 10 - 2.5, r2 = 3, h = 4);
      }

    }

    
    translate([0, 0, -13])rotate([-angle, 0, 0])
    fingercutout(45,20);
    
    translate([0, 0, 0])cylinder(d = 28.8, h = 10);
    translate([-3, 11.5, -2])cube([6, 2.5, 10]);
    translate([-3, 11.5, -2])cube([6, 5, 10]);
  }
}



module fingercutout(angle,height){
    translate([0,0,-height])cylinder(d=20,h=height);
    translate([0,0,0])sphere(d=20);
    translate([0,0,-height])sphere(d=20);
    rotate([0,0,angle/2])translate([-40,0,0])
    union() {
      rotate([0, 90, 0])cylinder(d = 20, h = 40);
       translate([0,0,-height])rotate([0, 90, 0])cylinder(d = 20, h = 40);
       translate([0,-10,-height])cube([40,20,height]); 
    }

    rotate([0,0,-angle/2])translate([0,0,0])
        union() {
      rotate([0, 90, 0])cylinder(d = 20, h = 40);
      translate([0,0,-height])rotate([0, 90, 0])cylinder(d = 20, h = 40);
                  translate([0,-10,-height])cube([40,20,height]);
    }
}    

module originalhandle() {
  difference() {
    union() {

      hull() {
        cylinder(d = 32, h = 2);
        translate([0, -15, -35])rotate([80, 0, 0])cheese(r1 = 10 - 2.5, r2 = 3, h = 4);
      }

    }
    translate([0, 0, 0])cylinder(d = 28.8, h = 10);
    translate([-20, 0, -11])rotate([-10, 0, 0])

    union() {
      rotate([0, 90, 0])cylinder(d = 20, h = 40);
      translate([0, -10, -60])cube([40, 20, 60]);
    }
    translate([-3, 11.5, -5])cube([6, 2.5, 10]);
  }
}

//translate([-40,0,0])cylinder(d=24,h=8);
module cup(x,y){translate([0, 0, 5])rotate([x,y, 0]) {
  translate([0, 0, 5]) {
    translate([0, 0, 14]) {
      difference() {
        cheese(6.5, 2.5, 0);
        translate([0, 0, 26])sphere(d = 50);
      }
    }
    translate([0, 0, 5])cylinder(d = 9, h = 8);
    translate([0, 0, -7])difference() {
      sphere(d = 28);
      translate([-15, -15, -15])cube([30, 30, 22]);
    }
  }
}
}



module potmeters(){
translate([-3,2,0])cube([23,10,14]);

translate([2,1,0])cube([10,16,14]);

cube([14,14,14]);

}




module doughnut(r1, r2, h) {
  rotate_extrude() {
    hull() {
      translate([r1, h, 0])circle(r = r2);
      translate([r1, 0, 0])circle(r = r2);
    }
  }
}

module cheese(r1, r2, h) {
  hull() {
    rotate_extrude() {
      translate([r1, h, 0])circle(r = r2);
      translate([r1, 0, 0])circle(r = r2);
    }
  }
}

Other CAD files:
remote-modular-ps4/export/rounded_version_half_mesh2.stl
remote-modular-ps4/export/modularremote-beugelring-19.stl

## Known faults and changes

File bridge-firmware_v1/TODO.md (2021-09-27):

# To do:

## In: bridge-firmwareOOP_incl_configv2

### Firmware code explanation

The UML diagram in this folder "splitcontroller_UML_diagram.png" shows the structure of the code.

- Initially an instance of "Nunchuckcontr" or "Modps4contr" is created based on which is defined. These are derived classes with "Controller" as base class for the common basis.
- To utilise custom mapping, in the beginning of the program two sets of struct are defined: one for the custom CSV mapping and one for the pin allocation. Of these structs, a custom std::map is created that can be updated with updated CSV instances in use.
- A sample mapping is already defined. This is to avoid null errors when the program is run without uploading a CSV before. Also, this way the std::map has to be initialized only once.
- the mapping in the std::map is defined as follows:
```
std::map<custCSVmapping, PinAllocation> mPinAlloc =
{
  {{green,left ,none,joyRXax2,repeat},{"joyRXax2", 2, DIGITALPIN}},
  ...
```
I chose the custCSVmapping as key and the PinAllocation as value because this works better with searching the std::map and updating later
- The "Controller" class has a method "operate()" in which buttons are read. The code of "operate()" itself hasn't changed since the original firmware yet, but reading the values has to be adapted to the std::map. For instance:
```
switch(LeftMode)
```
 Has to be changed to read the std::map key struct "mode" element. It won't change the logic, just a matter of renaming the variables.

 - That's about most of it. The original program worked but this rewrite makes adaptation and extensions easier with the use of OOP.
 Also the library NunchuckFunctions is rewritten and optimised by omitting superfluous code.

### To do: firmware

- Finetune existing code
  - Clean up SDreader class. This was dummy code so it has to be adapted for this projects' purpose
  - Adapt SDreader class to browse CSV files on SD.
  - Clean up CSV reader class.
  - Implement std::map mPinAlloc updating in CSV reader class method. Loop through map to look for element with something similar to following concise code:
  ```
    for (auto & element : pinalloc) {
        // if element.btn == csvElement.assgndto {
      // append mPinAlloc, csvElement, element}
        element.doSomething ();
      }
      ```

  - Update Controller class and derived classes to use the mPinAlloc mapping instead of original m_ps4pins in "operate()" and other methods

### CSV GUI program, code explanation

The CSV GUI program is a program that enables the user to create a mapping CSV file in a user friendly manner.

It is written in Python for convenience. It uses PyQt5 as GUI library.
Pandas is used for data. It has a library method to read and write DataFrames to CSV. Pandas will be used within the program to process the data.

### To do: Additional program with GUI

- Program with GUI with form fields
- generate correct dropdown items per row (eg: menu: red, green, blue or newly created. Button: list of defined buttons of the splitcontroller or ps4)
- Regex input validation
- I advise to make use of pyinstaller after completion of the script to make installation for the client easier.

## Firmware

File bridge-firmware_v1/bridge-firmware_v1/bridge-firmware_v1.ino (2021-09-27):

/*************************************************************
  TODO adjust map references for m_ps4pins


   Sketch for controlling a modified PS4 controller
   using two nunchucks or analog nunchuck equivalent
   (two hand-held controllers with two axis and two buttons)

   2 nunChucks (multiplexed) using code from WiiChuckDemo by
   2008 Tod E. Kurt, http://thingm.com/

   Controller is Arduino Due, 1k series resistors are used
   between PS4 buttons and Due outputs. All inputs are active-low
   except R1, L1 and the Z-axes.

   AnalogWrite is used to mimick joystick signals, RC low-pass
   filters (10uF, 1k) have been used to make the analog signals


   E13 - November 2020
   --

   Original nunchuck:  signal:    ext. cable    black nunchuck:
   white -             ground     orange        white
   red -               3.3+v      black         red
   green -             data  A4   blue          blue
   yellow -            clock A5   red           green

   PCA 9540 pinout
         _____
   SCL -|     |- SC1
   SDA -|     |- SD1
   VCC -|     |- GND
   SD0 -|_____|- SC0

   both the nunchucks and the PCA95040 can be powered from pins, 5V
   For I2C using internal pull-up is sufficient

   for the wired handheld controllers the following pinout
   has been used: on RJ45 connectors:

   1 analog_X
   2 analog_Y
   3 VCC
   4 GND (switch)
   5 GND (switch)
   6 GND (potentiometer)
   7 switch_1
   8 switch_2

 **************************************************************/

//  arduino-cli compile --fqbn arduino:sam:arduino_due_x_dbg bridge-firmwareOOP &>> debuglog.txt
// arduino-cli upload -p /dev/ttyACM0 -b arduino:sam:arduino_due_x_dbg -i <sketchname>.arduino.sam.arduino_due_x_dbg.bin
//arduino-cli compile  --fqbn arduino:sam:arduino_due_x_dbg bridge-firmwareOOP
//arduino-cli compile --fqbn arduino:sam:arduino_due_x bridge-firmwareOOP

//#define NUNCHUCK (1)
//#define DEBUG (1)
#include <Arduino.h>

#include <Adafruit_NeoPixel.h>
#include <ArduinoSTL.h>

#include <iostream>
#include <map>
#include<vector>
#include<iterator>

// below is for reading CSV files from SD
#include <limits.h>


// below are for ReprapDiscount Smart Controller
#include <SPI.h>
#include <SD.h>
#include <LiquidCrystal.h>

#define CS_PIN SS

File file;

// define 1 if nunchuck, 0 if PS4 mod
#define NUNCHCK 1

// define 1 if SD/LCD module present
#define SDCLDMODULE 1

Adafruit_NeoPixel leftRing = Adafruit_NeoPixel(12, 53, NEO_GRB + NEO_KHZ800);
Adafruit_NeoPixel rightRing = Adafruit_NeoPixel(12, 51, NEO_GRB + NEO_KHZ800);

enum Device {NUNCHUCK, PS4CONTR};

#if NUNCHCK > 0
#include <NunchuckFunctions.h>
NunchuckFunctions* nunchuckFunctions = new NunchuckFunctions;
const Device dv = NUNCHUCK;
#else
const Device dv = PS4CONTR;
#endif

enum Mode {GREEN, RED, BLUE};
enum Side {LEFT, RIGHT};
enum PinType {DIGITALPIN, ANALOGPIN, PWMPIN};
enum SplitContrButtons {JLJOY, RJOY, LBTN1, LBTN2, RBTN1, RBTN2};

const uint8_t greenLED = 13;
const uint8_t redLED = 12;

struct PinAllocation {
  std::string     btn;
  uint8_t           pinnum;
  PinType         pinType;
  std::string     mappedps4func;
  bool operator==(const PinAllocation& r) const   {
    return btn == r.btn;
  }
};

struct custCSVmapping
{
  std::string menu;
  std::string side;
  std::string btn;
  std::string assgndto;
  std::string mode;
};


std::vector<PinAllocation> pinalloc =
{
  {"joyRXax2", 2, DIGITALPIN},
  {"joyRYax1", 3, DIGITALPIN},
  {"joyRZb11", 4, DIGITALPIN},
  {"joyLZb12", 7, DIGITALPIN},
  {"joyLYax4", 6, DIGITALPIN},
  {"joyLXax3", 5, DIGITALPIN},
  {"sqbutton", 26, DIGITALPIN},
  {"circbutton", 28, DIGITALPIN},
  {"psbutton", 30, DIGITALPIN},
  {"l2button", 32, DIGITALPIN},
  {"r2button", 34, DIGITALPIN},
  {"tributton", 36, DIGITALPIN},
  {"xbutton", 38, DIGITALPIN},
  {"lhat", 40, DIGITALPIN},
  {"rhat", 42, DIGITALPIN},
  {"uhat", 44, DIGITALPIN},
  {"dhat", 46, DIGITALPIN},
  {"r1button6", 48, DIGITALPIN},
  {"l1button5", 50, DIGITALPIN},
  {"optbutton",  52, DIGITALPIN},
  {"shrebutton", A8, DIGITALPIN},
  {"accx1", A5, ANALOGPIN},
  {"accy1", A4, ANALOGPIN},
  {"accx2", A1, ANALOGPIN},
  {"accy2", A0, ANALOGPIN},
  {"c_button1", A6, ANALOGPIN},
  {"z_button1", A7, ANALOGPIN},
  {"c_button2", A2, ANALOGPIN},
  {"z_button2", A3, ANALOGPIN},
  {"PWM1", 2, PWMPIN},
  {"PWM2", 3, PWMPIN},
  {"PWM3", 5, PWMPIN},
  {"PWM4", 6, PWMPIN},
  {"PWM5", 7, PWMPIN}
};

std::map<custCSVmapping, PinAllocation> mPinAlloc =
{
  {{green,left ,none,joyRXax2,repeat},{"joyRXax2", 2, DIGITALPIN}},
  {{green,left ,none,joyRYax1,repeat},{"joyRYax1", 3, DIGITALPIN}},
  {{green,left ,none,joyRZb11,repeat},{"joyRZb11", 4, DIGITALPIN}},
  {{green,left ,none,joyLZb12,repeat},{"joyLZb12", 7, DIGITALPIN}},
  {{green,left ,none,joyLYax4,repeat},{"joyLYax4", 6, DIGITALPIN}},
  {{green,left ,none,joyLXax3,repeat},{"joyLXax3", 5, DIGITALPIN}},
  {{green,left ,none,sqbutton,repeat},{"sqbutton", 26, DIGITALPIN}},
  {{green,left ,none,circbutton,repeat},{"circbutton", 28, DIGITALPIN}},
  {{green,left ,none,psbutton,repeat},{"psbutton", 30, DIGITALPIN}},
  {{green,left ,none,l2button,repeat},{"l2button", 32, DIGITALPIN}},
  {{green,left ,none,r2button,repeat},{"r2button", 34, DIGITALPIN}},
  {{green,left ,none,tributton,toggle},{"tributton", 36, DIGITALPIN}},
  {{green,left ,none,xbutton,toggle},{"xbutton", 38, DIGITALPIN}},
  {{green,left ,none,lhat,toggle},{"lhat", 40, DIGITALPIN}},
  {{green,left ,none,rhat,toggle},{"rhat", 42, DIGITALPIN}},
  {{green,left ,none,uhat,toggle},{"uhat", 44, DIGITALPIN}},
  {{green,left ,none,dhat,toggle},{"dhat", 46, DIGITALPIN}},
  {{green,left ,none,r1button6,toggle},{"r1button6", 48, DIGITALPIN}},
  {{green,left ,none,l1button5,toggle},{"l1button5", 50, DIGITALPIN}},
  {{green,left ,none,optbutton,toggle},{"optbutton",  52, DIGITALPIN}},
  {{green,left ,none,accx1,toggle},{"shrebutton", A8, DIGITALPIN}},
  {{green,left ,none,accy1,toggle},{"accx1", A5, ANALOGPIN}},
  {{green,left ,none,accx2,toggle},{"accy1", A4, ANALOGPIN}},
  {{green,left ,none,accy2,toggle},{"accx2", A1, ANALOGPIN}},
  {{green,left ,none,c_button1,toggle},{"accy2", A0, ANALOGPIN}},
  {{green,left ,none,z_button1,toggle},{"c_button1", A6, ANALOGPIN}},
  {{green,left ,none,c_button2,toggle},{"z_button1", A7, ANALOGPIN}},
  {{green,left ,none,z_button2,toggle},{"c_button2", A2, ANALOGPIN}},
  {{green,left ,none,z_button2,toggle},{"z_button2", A3, ANALOGPIN}},
  {{green,left ,none,PWM1,toggle},{"PWM1", 2, PWMPIN}},
  {{green,left ,none,PWM2,toggle},{"PWM2", 3, PWMPIN}},
  {{green,left ,none,PWM3,toggle},{"PWM3", 5, PWMPIN}},
  {{green,left ,none,PWM3,toggle},{"PWM4", 6, PWMPIN}},
  {{green,left ,none,PWM3,toggle},{"PWM5", 7, PWMPIN}}
};



unsigned long loopTime;

// buffers for the coloured rings:
unsigned char Abuffer[12];
unsigned char Bbuffer[12];
unsigned char Cbuffer[12];
unsigned char Dbuffer[12];
boolean L1state, R1state, R2state, L2state, Rreleased;
boolean LeftReleased, RightReleased;

// this class needs to be cleaned up, it hasn't been adjusted to this projects' purpose
class SDreader {
  private:
    const uint8_t BUTTON = 41;
    const uint8_t BTN_EN1 = 31;
    const uint8_t BTN_EN2 = 33;
    const uint8_t BTN_ENC = 35;
    const uint8_t BUZZER = 37;
    const uint8_t SDCARDDETECT = 49;
    const uint8_t SLAVESELECT = 53;
    volatile uint8_t position;
    File root;
    const uint8_t rs = 16, en = 17, d4 = 23, d5 = 25, d6 = 27, d7 = 29;
    LiquidCrystal lcd;

    //    static stringstream ss;

  public:
    SDreader() : lcd(rs, en, d4, d5, d6, d7) {
      pinMode(BUZZER, OUTPUT);
      pinMode(BUTTON, INPUT_PULLUP);
      pinMode(BTN_ENC, INPUT_PULLUP);
      pinMode(BTN_EN1, INPUT_PULLUP);
      pinMode(BTN_EN2, INPUT_PULLUP);
      pinMode(SDCARDDETECT, INPUT_PULLUP);

      // set up the LCD's number of columns and rows:
      lcd.begin(20, 4);
      // Print a message to the LCD.
      lcd.print("Initializing SD card...");
      if (!SD.begin(SLAVESELECT)) {
        lcd.print("initialization failed!");
        while (1);
      }
      lcd.print("initialization done.");
      root = SD.open("/");
      printDirectory(root, 0);
      lcd.print("done!");
      // here: go to function to read data
    }


    void readData() {
      // while true? except stop
      static unsigned long looptimer; // for timing in this loop.
      encoder();  // run the service routine, could also be using timer uint8_terrupt
      if (millis() > looptimer + 99) {
        looptimer = millis();
        lcd.setCursor(0, 1); // line 1 is the second row, since counting begins with 0
        lcd.print(millis() / 1000); // print the number of seconds since reset:
        if (!digitalRead(BTN_ENC)) position = 0; // reset encoder when pressed
        lcd.setCursor(5, 1);
        lcd.print(position);
        lcd.print("    "); // clean up after long numbers have been printed
        digitalWrite(BUZZER, !digitalRead(BUTTON)); // beep beep beep....
        lcd.setCursor(10, 1);
        lcd.print(digitalRead(SDCARDDETECT)); // just for checking. It could be part of
        // a better routine checking a card has been inserted and (re)connecting.
      }
    }


    void encoder() {
      uint8_t A = digitalRead(BTN_EN1);
      uint8_t B = digitalRead(BTN_EN2);
      static uint8_t dA, dB;
      // full quadrature, so 4 values per 'click'
      if ((A == 1 && dA == 0 && B == 0) || (A == 0 && dA == 1 && B == 1) || (B == 1 && dB == 0 && A == 1) || (B == 0 && dB == 1 && A == 0)) position++;
      if ((B == 1 && dB == 0 && A == 0) || (B == 0 && dB == 1 && A == 1) || (A == 1 && dA == 0 && B == 1) || (A == 0 && dA == 1 && B == 0)) position--;
      dA = A; // store previous values
      dB = B; // store previous values
    }

    void printDirectory(File dir, int numTabs) {
      while (true) {
        File entry =  dir.openNextFile();
        if (! entry) {
          // no more files
          break;
        }
        for (uint8_t i = 0; i < numTabs; i++) {
          Serial.print('\t');
        }
        Serial.print(entry.name());
        if (entry.isDirectory()) {
          Serial.println("/");
          printDirectory(entry, numTabs + 1);
        } else {
          // files have sizes, directories do not
          Serial.print("\t\t");
          Serial.println(entry.size(), DEC);
        }
        entry.close();
      }
    }
};


class CSVreader {
  protected:
    File csvfile;
    custCSVmapping cstmMapping;

  public:
    //std::vector <custCSVmapping> allcstmMappings;
    std::string menu, side, button, assigndto, mode;

    CSVreader() {
      SDreader sdreader;

      // sdreader -> callfunc();
    }

    void readVals() {
      while (csvfile.read()) {
        getline(csvfile, menu, ',');
        getline(csvfile, side, ',') ;
        getline(csvfile, button, ',') ;
        getline(csvfile, assigndto, ',');
        getline(csvfile, mode, '\n');
      }
    }
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

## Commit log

2021-01-15 Add files via upload
    First commit: rough (but the 1.0 tried, tested and deployed) files
    [handle.stl, modularremote-beugelring-18.4.stl, modularremote-beugelring-19.stl, modularremote-beugelring.stl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]
2021-01-18 switch-joystick version added
    added also the files for a handheld based on the nintendo-switch joystick
    [joycon.stl, modularremoteswitch.scad, switch-holder.stl, switch-top.stl]
2021-02-01 first contrib
    [joycon.stl, modularremoteswitch.scad, switch-holder.stl, switch-top.stl]
2021-02-24 another update
    [fingercutout.FCStd, fingercutout_contour.dxf, handle_edit.scad]
2021-06-16 Removed files from the index (now ignored)
    [fingercutout.stl, half_mesh1.stl, half_mesh2.stl, handle_3v6.f3z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]
2021-09-15 updating. Again
    [format_config_file.csv, format_config_file.ods, test_config_file.csv]
